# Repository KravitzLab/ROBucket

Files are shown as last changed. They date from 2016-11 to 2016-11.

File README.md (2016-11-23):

# ROBucket
```C
PAGE UNDER CONSTRUCTION
```
## What is it?
[description] a low-cost operant chamber based on the Arduino microcontroller

## What's available?
+ <b> ROBucket-wiki </b>  

Other links above:

+ <b>Build instructions</b>  
-Detailed instructions for assembling your own ROBucket!

+ <b>Design files</b>  
-Side panel templates for drilling mounting holes  
-3D design files for interior operant mount

+ <b>Arduino code</b>  
-Various scripts (Arduino sketches) for different experiment paradigms

ROBucket was designed by a team of researchers at the National Institutes of Health, more info here: http://www.kravitzlab.com/

https://tinkercad.com/things/8v2CjPmA2EL

Check out our site [here](https://www.niddk.nih.gov/research-funding/at-niddk/labs-branches/diabetes-endocrinology-and-obesity-branch/eating-addiction-section/rodent-operant-bucket/Pages/default.aspx)

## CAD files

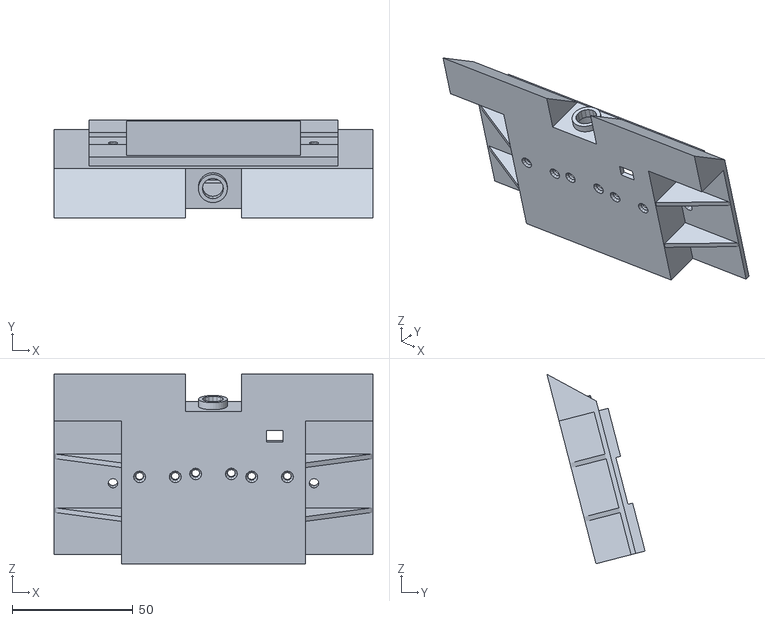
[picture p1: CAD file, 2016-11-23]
Design-files/ROBucket nose poke housing.stl
132.0 x 40.6 x 78.4

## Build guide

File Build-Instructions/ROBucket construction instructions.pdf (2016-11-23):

# Instructions for Constructing a Rodent Operant Bucket (ROBucket)

### Required Parts

Part | Quantity Source | Total Price
4 quart square container (6.5" x 6.5" x 8") | 1 | U.S. Plastic Corp | $5.97
Lid for 2- and 4-quart containers | 1 | U.S. Plastic Corp | $1.42
Arduino UNO - R3 | 1 | SparkFun Electronics | $24.95
LCD keypad shield for Arduino | 1 | DFRobot | $14.55
Adafruit assembled data logging shield for Arduino | 1 | Adafruit Industries | $19.95
Kingston 4GB microSD high capacity (microSDHC) card | 1 | Office Depot | $8.99
Photo interrupter board with GP1A57HRJ00f | 3 | Karlsson Robotics | $14.97
Sainsmart 2-channel 5V relay module | 1 | O'Neill Computer Products | $18.99
12 VDC solenoid valve | 1 | American Science & Surplus | $3.25
Clear acrylic squares 1/2" acrylic square | 1 | U.S. Plastic Corp | $0.24
JST SH jumper 3 wire assembly - 8" | 3 | SparkFun Electronics | $4.05
Faceplate, 3 port | 1 | Zoro Tools | $7.91
Machine screw,flat,4-40x1/2 L, nylon | 8 | Zoro Tools | $0.32
Hex nut, machine screw, 4-40, black, nylon | 12 | Zoro Tools | $0.32
Wall adapter power supply - 9VDC 650mA | 1 | SparkFun Electronics | $5.95
DC barrel jack adapter - female | 1 | SparkFun Electronics | $2.95
1/2" straight cannula blunt end tip (15 gauge) | 1 | Fisnar | $0.24
Male luer with lock ring x 1/8" hose barb, nylon | 1 | Cole-Parmer | $0.34
Male luer with lock ring x female luer coupler, PC | 1 | Cole-Parmer | $0.56
BD 20mL syringe with Luer-Lok tip | 1 | Allegro Medical | $0.51
Masterflex platinum-cured silicone tubing, L/S 16, 25 ft. | 0.5 Ft | Cole-Parmer | $1.18
Stor-All broom clip | 2 | Aubuchon Hardware | $3.38
Jumper wires premium 6" F/F | 9 | SparkFun Electronics | $2.99
Wing nut,6-32 | 2 | Grainger | $1.07
Machine screw, flat, SS, 6-32x1.5 L | 2 | Grainger | $0.29
2-way 2.1mm DC barrel jack splitter squid | 1 | Adafruit Industries | $2.95
0.1" (2.54mm) crimp connector housing: 1x1-pin | 9 | Karlsson Robotics | $0.21
Female crimp pins for 0.1" housings | 9 | Karlsson Robotics | $0.54
3D printed housing | 1 | Makerbot Replicator 2 Desktop 3D Printer | Variable
Total | | | $149.19

Step 1: Drilling holes in the bucket
1. Print out the Adobe Illustrator files for the front and side panel on plain paper or removable labels (8½” x 11”).
2. Place the templates on the bucket, with the side panel to the right of the front panel.
3. Drill seven 1

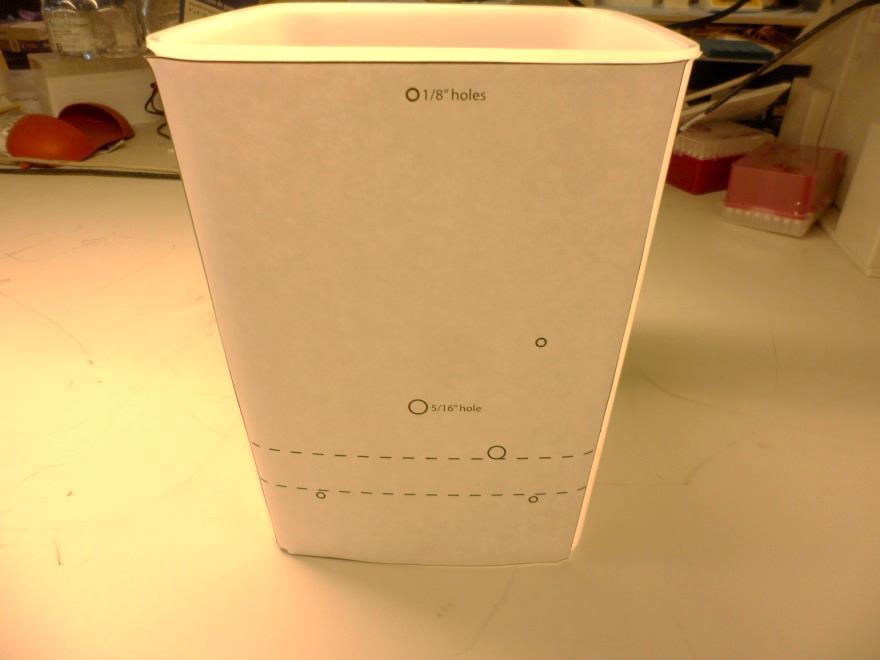
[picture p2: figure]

/8” holes and two 5
/16” holes where shown on the templates.
Step 2: Assembling the nose poke and drinking well enclosure

In this step, we will assemble the nose poke and drinking well enclosure and attach it to the inside of the bucket.

1. Print out the 3D housing. We used Makerbot PLA material and printed at a high resolution.

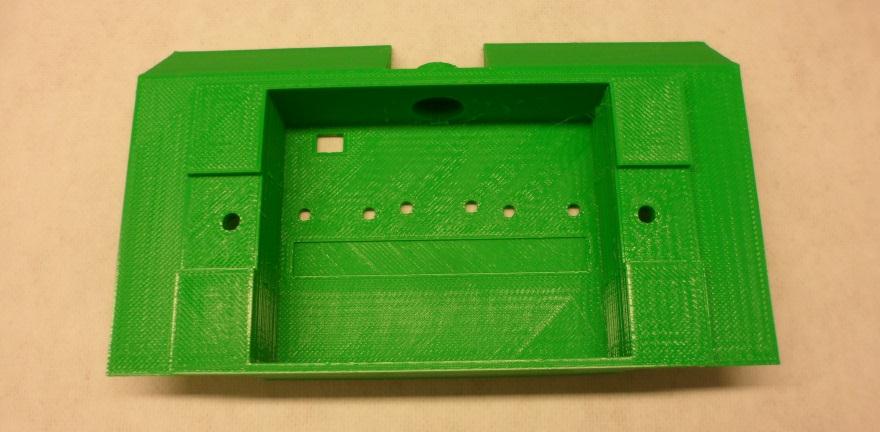
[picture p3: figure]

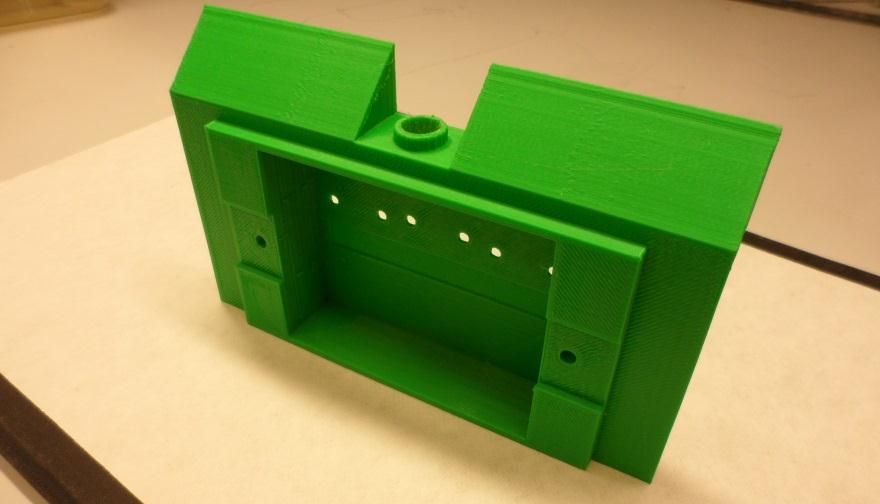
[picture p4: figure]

2. Plug three JST SH jumper 3-wire assemblies into three photo interrupter boards. Label the signal wire for each “L” (for left), “C” (for center), and “R” (for right).

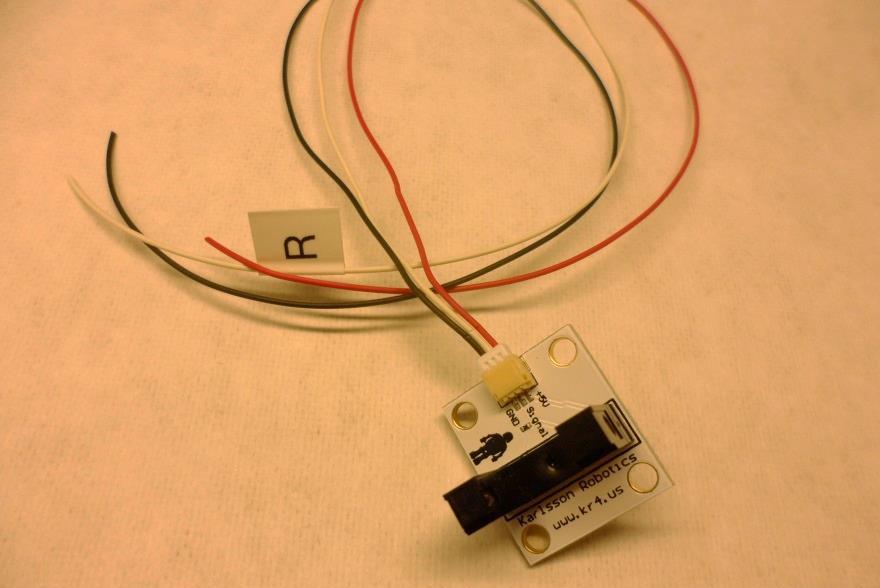
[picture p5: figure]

3. Use the nylon screws and hex nuts to secure the photo interrupter boards to the inside of the 3D printed cover and bring the wires to the outside of the cover using the hole in the top left of the housing.

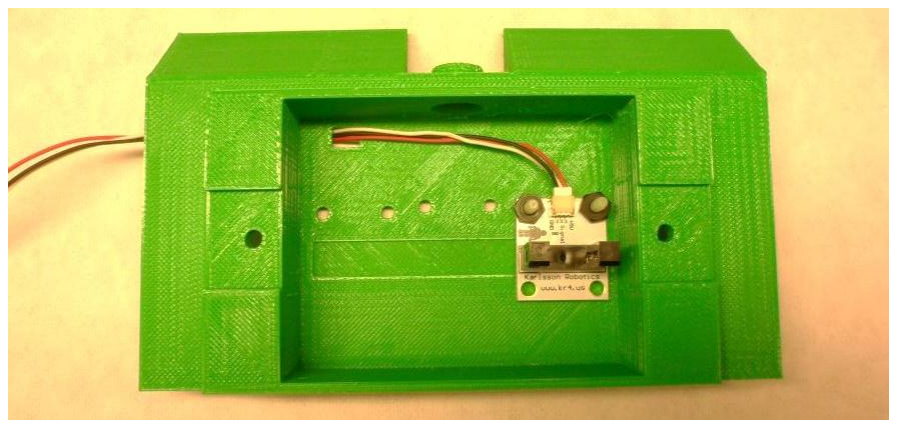
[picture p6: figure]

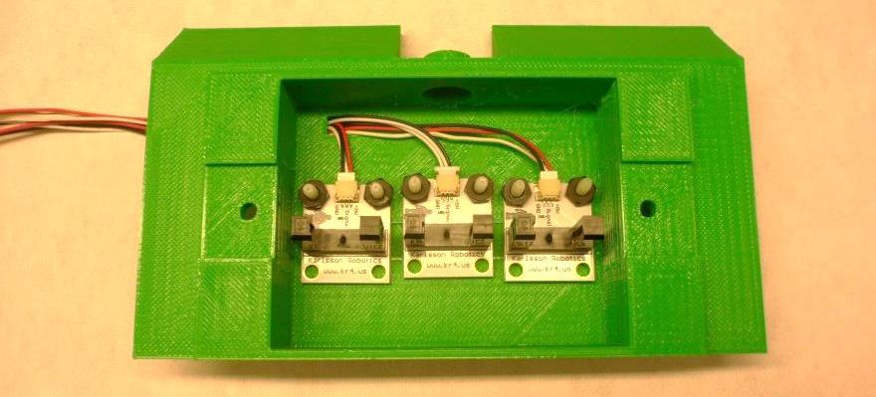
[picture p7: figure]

4. Assemble the blunt needle with the two luer lock pieces, and screw together securely in the top hole in the housing.

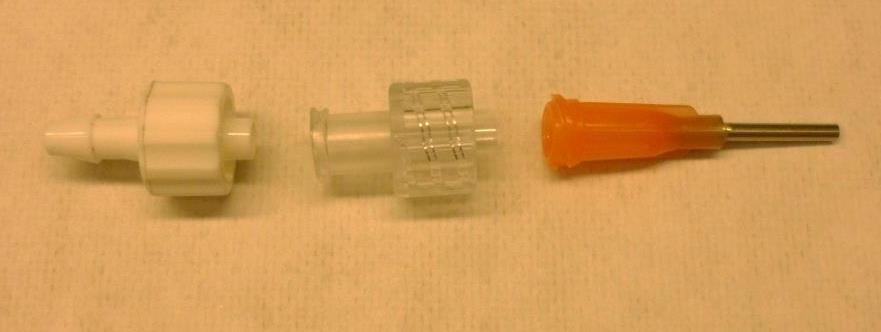
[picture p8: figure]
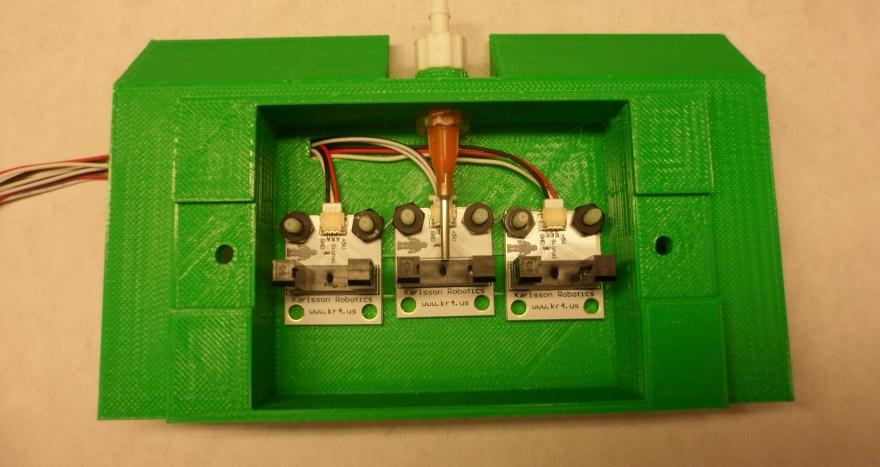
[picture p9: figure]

5. Place the ½” piece of plastic under the center poke.

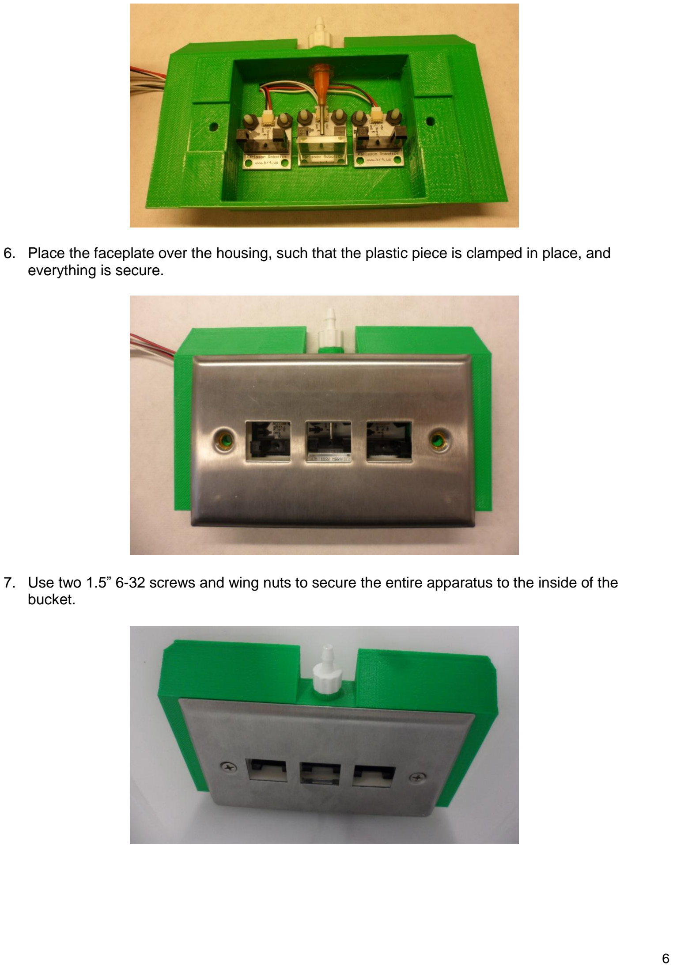
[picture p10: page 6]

6. Place the faceplate over the housing, such that the plastic piece is clamped in place, and everything is secure.
7. Use two 1.5” 6-32 screws and wing nuts to secure the entire apparatus to the inside of the bucket.

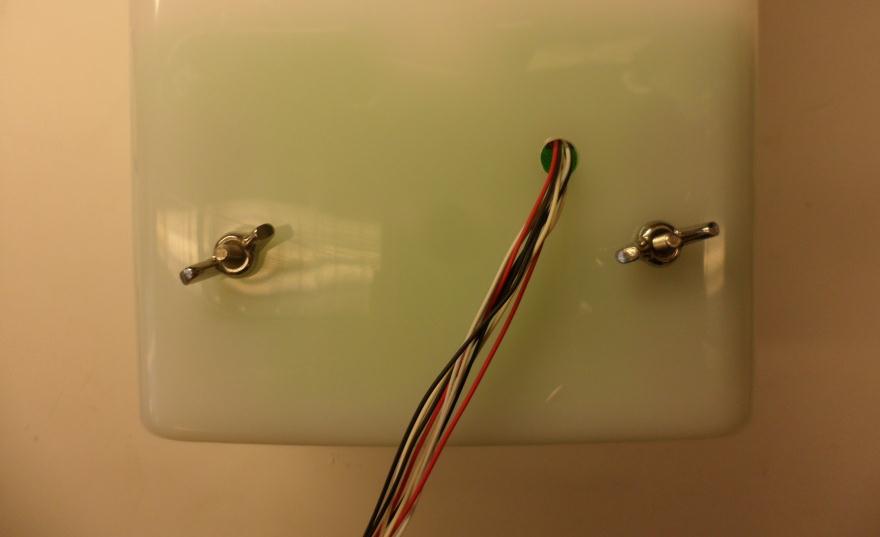
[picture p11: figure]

Step 3. Mounting the solenoid valve

In this step, we will mount the solenoid valve and liquid syringe on the outside side of the bucket.

1. Using nylon screws and hex nuts, attach the two broom clips to the two 5/16” holes on the side of the bucket.

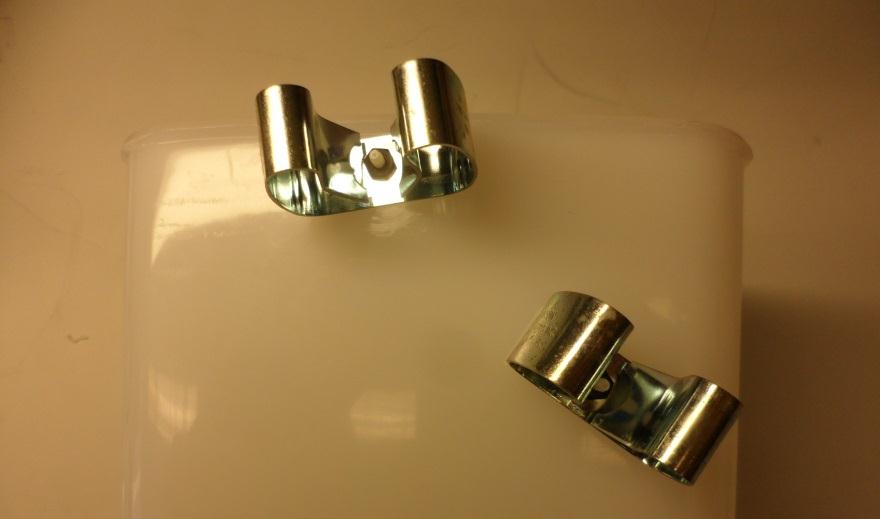
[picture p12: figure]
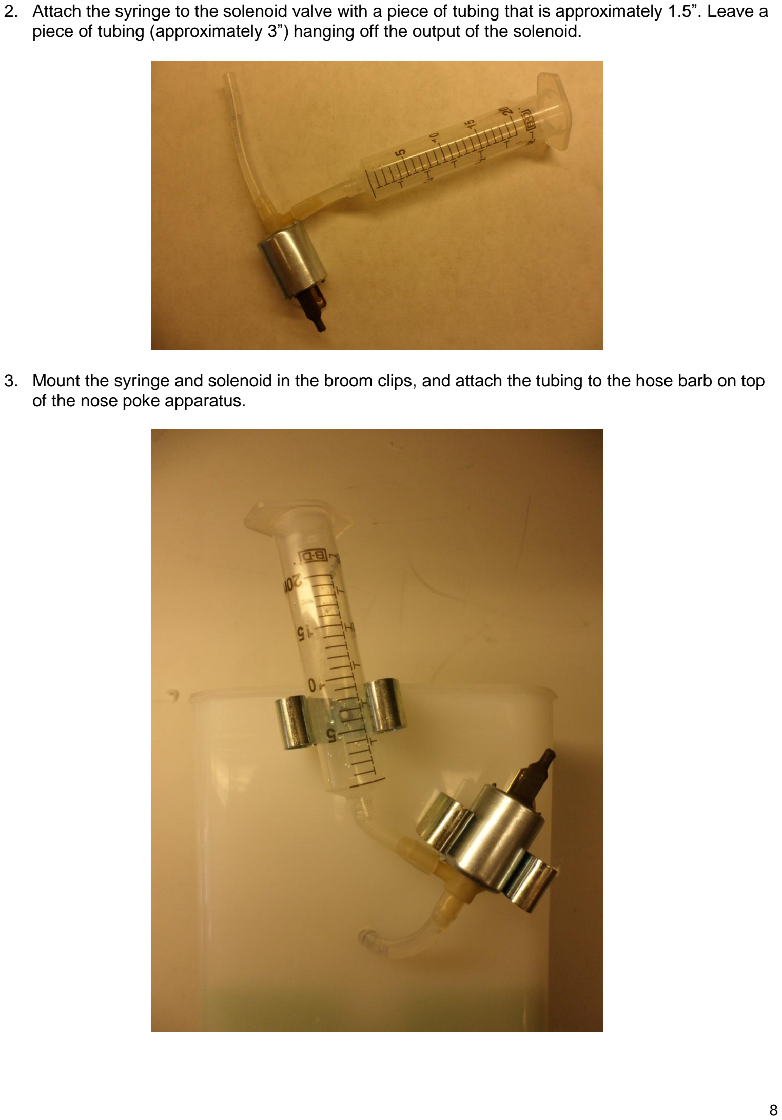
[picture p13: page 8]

2. Attach the syringe to the solenoid valve with a piece of tubing that is approximately 1.5”. Leave a piece of tubing (approximately 3”) hanging off the output of the solenoid.
3. Mount the syringe and solenoid in the broom clips, and attach the tubing to the hose barb on top of the nose poke apparatus.

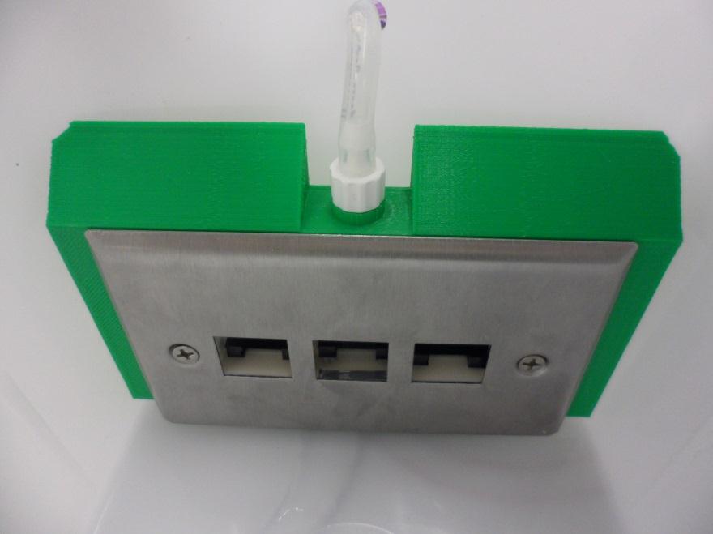
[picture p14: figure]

Step 4. Assembling the side panel electronics

In this step, we will assemble the side panel electronics and attach them to the outside front of the bucket.

1. Place the Arduino Uno so that the top right and bottom left mounting holes align with the top two holes in the side panel. Secure the Arduino board in place using the nylon screws and hex nuts. Place an additional hex nut between the bucket and the board at each mounting point, to allow for a small space between the Arduino and the bucket.

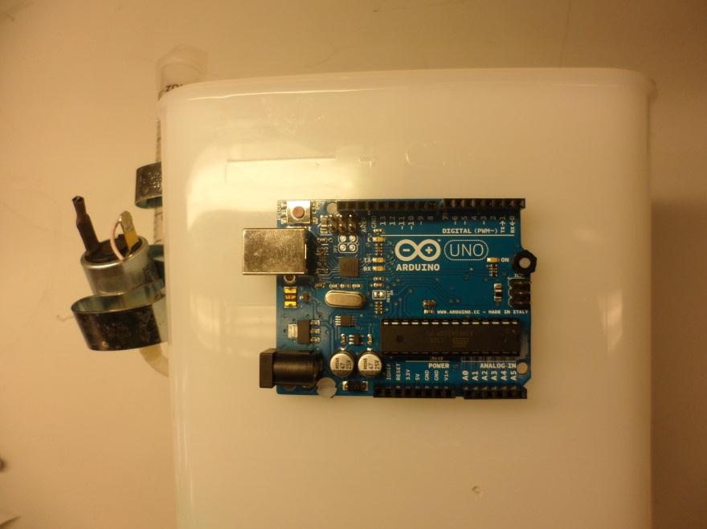
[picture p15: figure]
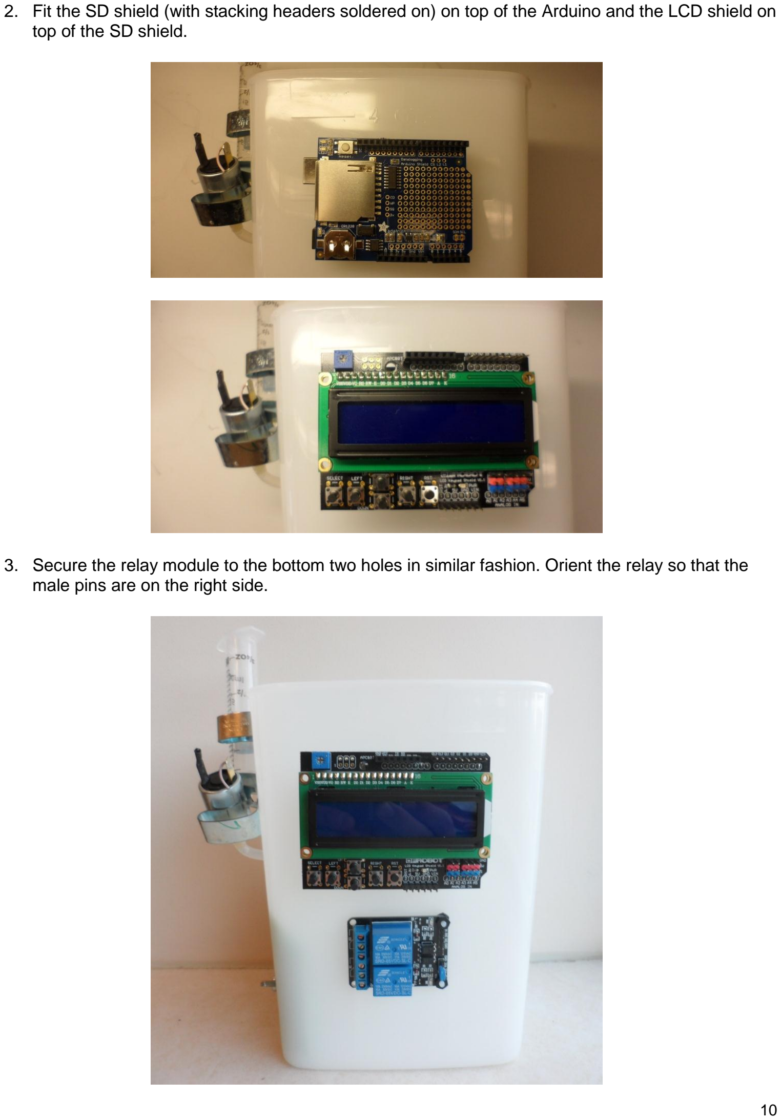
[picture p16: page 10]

2. Fit the SD shield (with stacking headers soldered on) on top of the Arduino and the LCD shield on top of the SD shield.
3. Secure the relay module to the bottom two holes in similar fashion. Orient the relay so that the male pins are on the right side.

Step 5. Wiring up the front electronics
In this step, we will wire up the front electronics.
1. Place three short pieces of heat shrink tubing around the bundle of 9 wires coming from the nose poke apparatus. Do not heat shrink these yet.

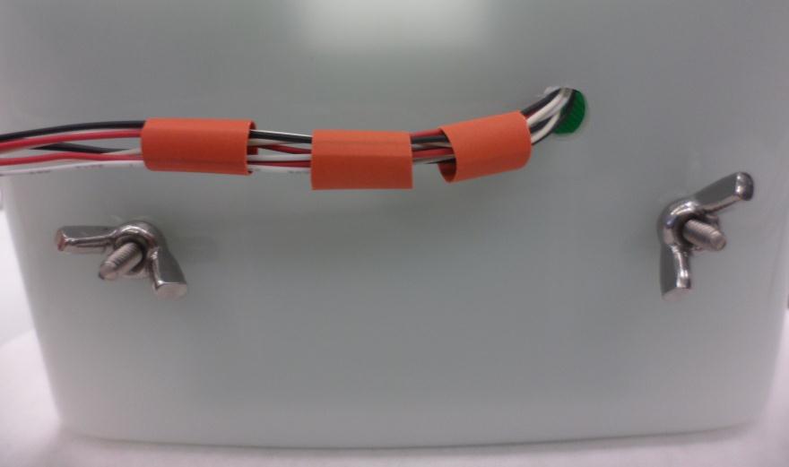
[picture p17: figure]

2. Route this bundle of wires underneath the relay module (you may want to unscrew it to do this).

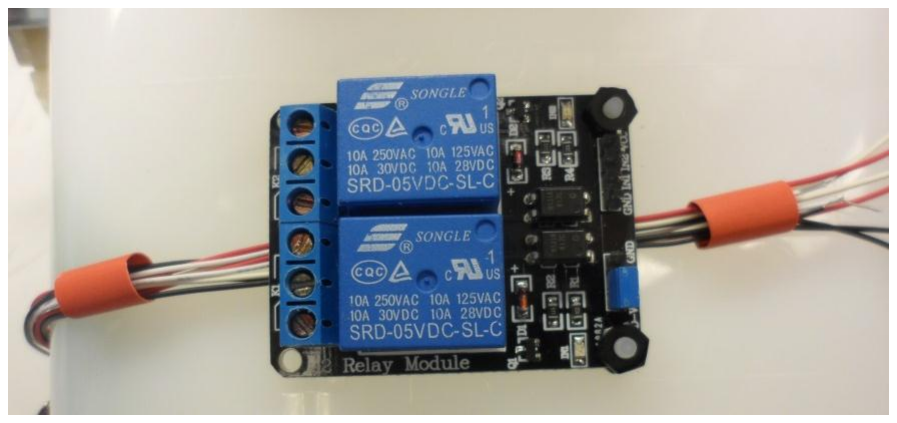
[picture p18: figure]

3. If these wires are long enough to reach the LCD keypad shield, place a crimp connector on the end of each.

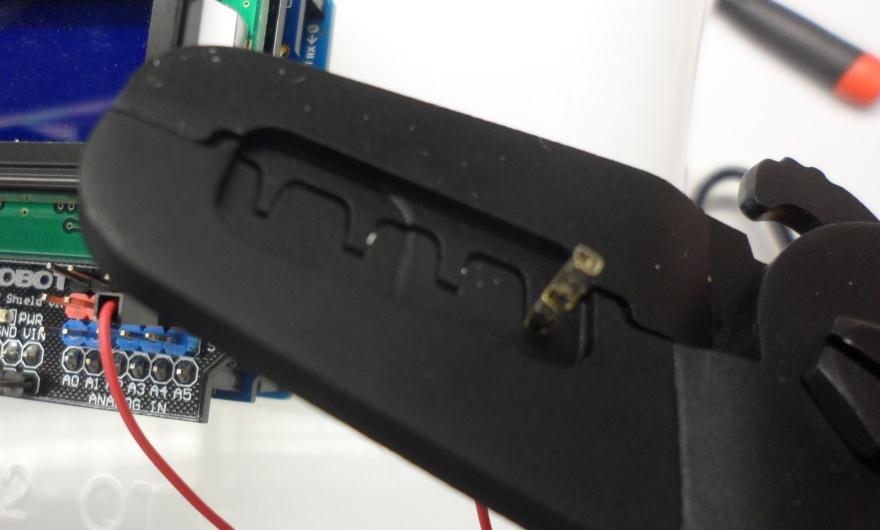
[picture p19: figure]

4. If any wires are not long enough, solder a header wire with a crimp connector on it to increase the length so it can reach.

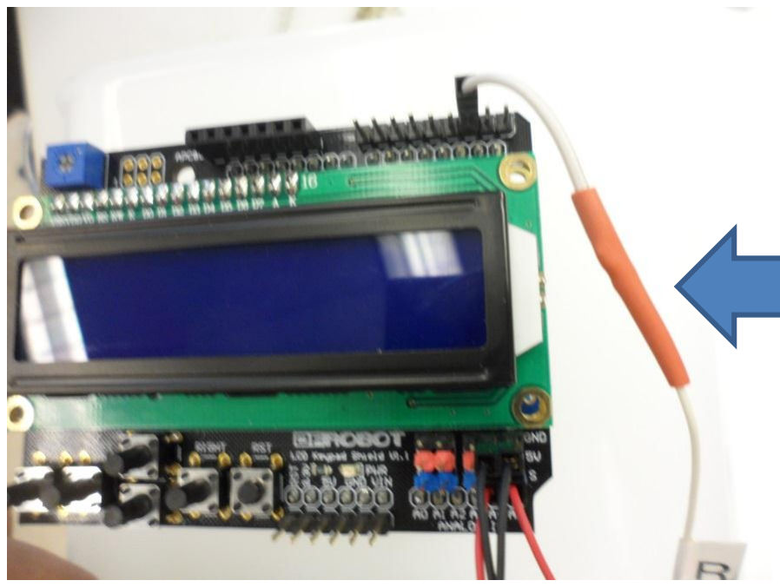
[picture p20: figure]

5. Plug the power and ground wires from the three nose pokes (6 wires total) into the power distributor on the LCD shield, such that each one has its own power and ground.

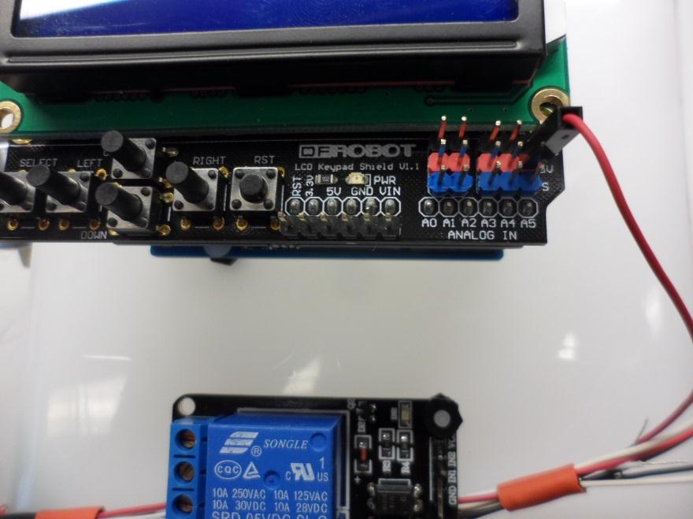
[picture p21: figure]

6. Plug the remaining 3 wires from the nose poke enclosure into the input/output pins at the top of the LCD shield, in the following order:
Pin 0: Active poke (left)
Pin 1: Drinking well (center)
Pin 2: Inactive poke (right)
7. Use three F/F jumper wires to connect the relay module to the GND and 5V pins on the LCD shield, and attach IN1 on the relay module to Pin 3 on the LCD shield.

Step 6. Wiring up the solenoid (almost done!)
1. Cut and strip one red wire approximately 7” long, and one red and one black wire, each approximately 4.5” long.
2. Solder the long red wire, and one of the black wires onto the solenoid, and heat shrink terminals.

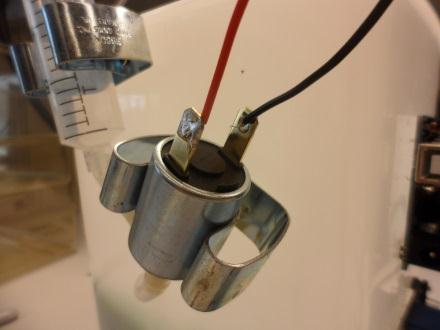
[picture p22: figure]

3. Screw the long red wire into the bottom port of the relay module, and the short red wire into the port that’s 2nd from the bottom.

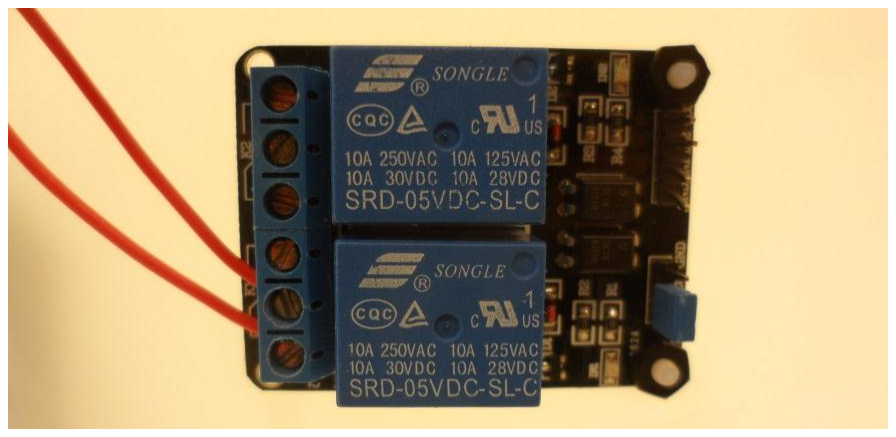
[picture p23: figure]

4. Screw the black wire from the solenoid, and the short red wire into the DC barrel jack.

5. Plug the barrel jack Y adapter into the DC barrel jack and the Arduino power input, and attach to a 9V DC, 650 mA power supply.

### 6. You’re done!

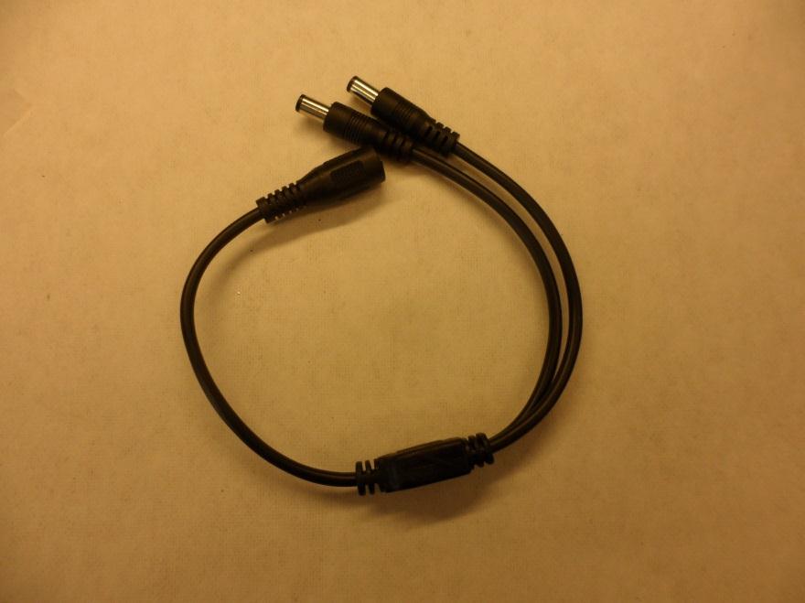
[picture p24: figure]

Step 7: Uploading the ROBucket program and testing the hardware
1. Download the ROBucket sketch from the website. Robucket_1poke.ino is for ROBuckets that only have an active poke and a drinking well, whereas Robucket_2pokes.ino is for ROBuckets that have both an active and inactive poke.
2. Upload the sketch to the Arduino Uno with a USB (Type B) cable.
3. Insert an SD or microSD card into the data logging shield before turning the ROBucket on. ROBucket will display an error message (“Card Failed”) unless there is a functional SD card in the data logging shield.
4. Fill the syringe with water.
5. Power up the ROBucket. The first time you fill the syringe with water, you might need to hit the Reset button on the LCD shield a few times to run the water through the tubing.
6. Push the Up button to start the FR1 program.
7. Check that all three pokes register on the LCD screen, that the active poke dispenses water into the drinking well, and that the data is being properly logged onto the SD card.

# ROBucket Wiring Diagram

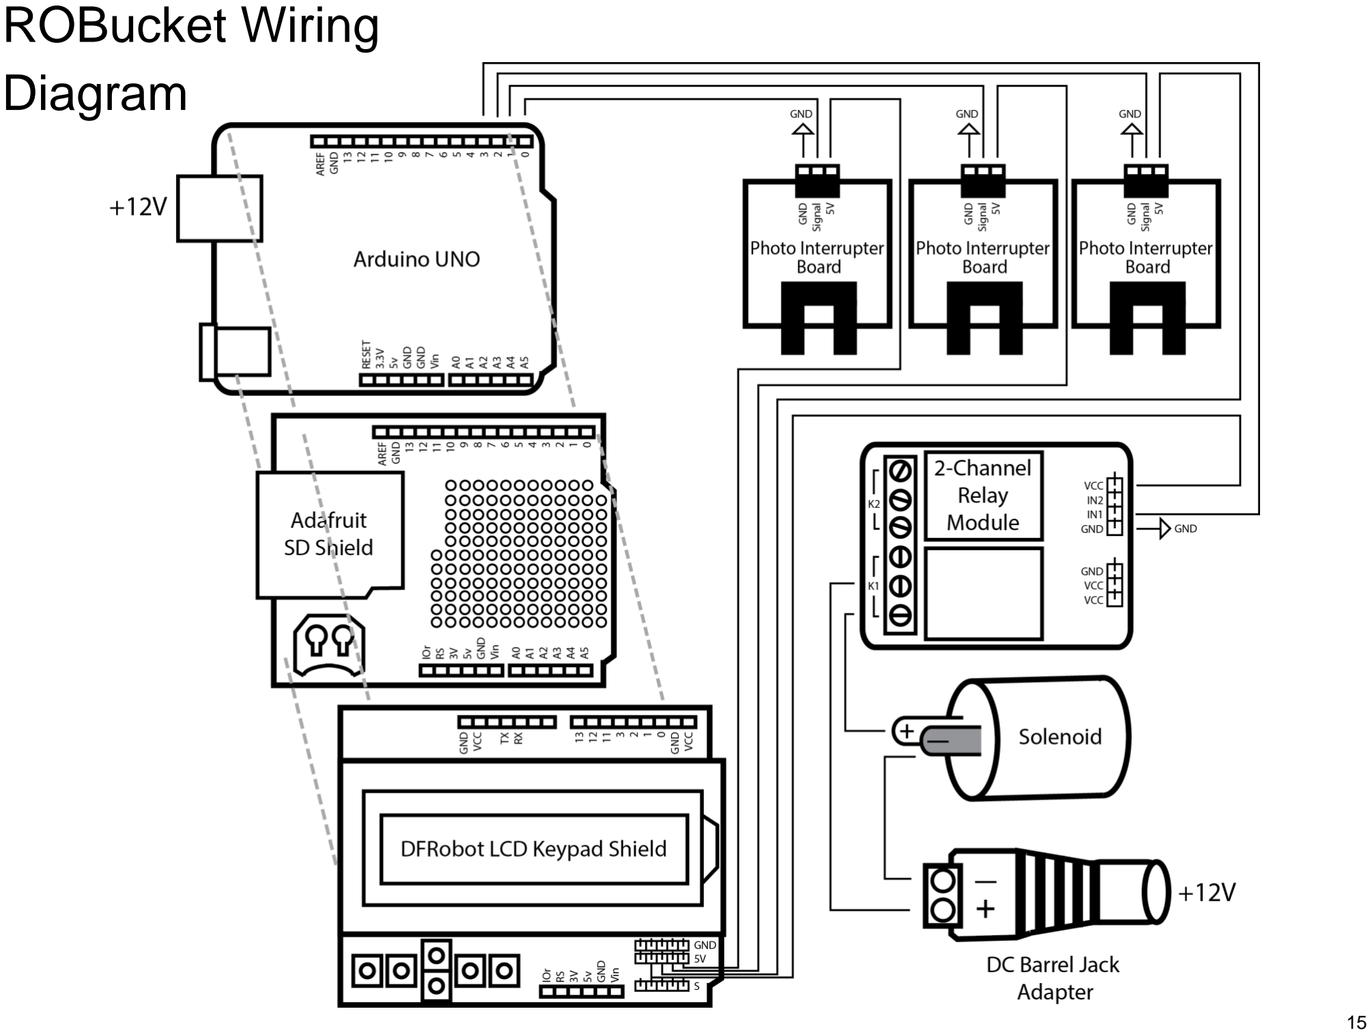
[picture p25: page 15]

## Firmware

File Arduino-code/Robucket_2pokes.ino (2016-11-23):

 #include <Wire.h>                                         // reference the Wire and LiquidCrystal libraries
 #include <LiquidCrystal.h>
 #include <SD.h>
 #include "RTClib.h"

const int activePin = 0;
const int drinkPin = 1; 
const int inactivePin = 2;
const int sugarPin = 3;
const int CS_pin = 10;

RTC_DS1307 RTC;

String year, month, day, hour, minute, second, date, time;

const int sugarAmt = 100;                                  // open the solenoid for 50 ms (controls amount of sucrose solution)
int timeOut = 1;                                    // set the timeout period between pokes to 1s

int activeState = 0;                                         // initialize counter variables to 0
int lastActiveState = 0;
int activeCount = 0;
int lastActiveCount = 0;
int inactiveState = 0;
int lastInactiveState = 0;
int inactiveCount = 0;
int drinkState = 0;
int lastDrinkstate = 0;
int drinkCount = 0;
int pelletNumber = 1;
              
int pokeTime = 0;                            
int ipokeTime = 0;
int startTime = 0;
long previousMillis = 0; 
int x = 0;

LiquidCrystal lcd( 8, 9, 4, 5, 6, 7 );
int ratio = 0;
int program = 0;

int logData() {
  DateTime datetime = RTC.now();
  year = String(datetime.year(), DEC);
  month = String(datetime.month(), DEC);
  day  = String(datetime.day(),  DEC);
  hour  = String(datetime.hour(),  DEC);
  minute = String(datetime.minute(), DEC);
  second = String(datetime.second(), DEC);
 
  //Concatenate the strings into date and time
  time = month + "/" + day + " " + hour + ":" + minute + ":" + second;
  
  File dataFile = SD.open("RoBucket.csv", FILE_WRITE);
  if (dataFile) {   
    dataFile.print(ratio);
    dataFile.print(",");
    dataFile.print(time);
    dataFile.print(",");
    dataFile.print(pelletNumber-1);
    dataFile.print(",");
    dataFile.print(activeCount);
    dataFile.print(",");
    dataFile.print(inactiveCount);
    dataFile.print(",");
    dataFile.println(drinkCount);
    dataFile.close();
  }
}

int deliverSugar() {
  lcd.setCursor(14, 0);            // move the LCD cursor to row 2, column 5
  lcd.print(pelletNumber);           // update the nosepoke count on the LCD
  digitalWrite(sugarPin, HIGH);   // send 5 volts through the sugar delivery pin
    lastActiveCount = activeCount;
  pelletNumber = pelletNumber + 1;
  delay(sugarAmt);
  if (program == 4) {
     ratio = round ((5 * exp (0.2 * pelletNumber)) - 5);
  }
  digitalWrite(sugarPin, LOW);
  delay(200);
}

void setup() {                
  // initialize the digital pins as output and input
  pinMode(activePin, INPUT_PULLUP);
  pinMode(drinkPin, INPUT);
  pinMode (inactivePin, INPUT);
  pinMode (sugarPin, OUTPUT);
  pinMode (CS_pin, OUTPUT);
  
  Wire.begin();
  RTC.begin();
  
  // set up the LCD
  lcd.begin(16, 2);
  lcd.clear();
  
  if (!SD.begin(CS_pin)) {
    lcd.print("Card Failed");
    while(1) {}
    }
  
  else {
  lcd.print("Up=FR1 Rght=Mag");
  lcd.setCursor(0,1);
  lcd.print("Down=FR5 Left=PR");
  
  File dataFile = SD.open("RoBucket.csv", FILE_WRITE);
  if (dataFile) {
    dataFile.println("Program,Time,Sugar Deliveries,Active Pokes,Inactive Pokes,Well Entries");
    dataFile.close();
    }
  }
}

void loop() { 
  if (analogRead(0) < 50) {
    lcd.clear();
    lcd.print("Mag");
    lcd.setCursor(12,0);
    lcd.print("S:0");
    lcd.setCursor(0,1);
    lcd.print("A:0  I:0  W:0");
    startTime = millis()/1000;
    program = 2;
    ratio = random(45,75);
   }
  else if (analogRead(0) < 400) {
    lcd.clear();
    lcd.print("FR1");
    lcd.setCursor(12,0);
    lcd.print("S:0");
    lcd.setCursor(0,1);
    lcd.print("A:0  I:0  W:0");
    startTime = millis()/1000;
    program = 1;
    ratio = 1;
  }
  else if (analogRead(0) < 600) {
    lcd.clear();
    lcd.print("FR5");
    lcd.setCursor(12,0);
    lcd.print("S:0");
    lcd.setCursor(0,1);
    lcd.print("A:0  I:0  W:0");
    startTime = millis()/1000;
    program = 3;
    ratio = 5;
  }
  else if (analogRead(0) < 650) {
    lcd.clear();
    lcd.print("PR");
    lcd.setCursor(12,0);
    lcd.print("S:0");
    lcd.setCursor(0,1);
    lcd.print("A:0  I:0  W:0");
    startTime = millis()/1000;
    program = 4;
    ratio = round ((5 * exp (0.2 * pelletNumber)) - 5);
   }
  
  long t = millis()/1000 - startTime;
  
  String timeStamp;
      int h = t / 3600;
      timeStamp += h;
      timeStamp += ":";
      t = t % 3600;
      int m = t / 60;
      timeStamp += m;
      timeStamp += ":";
      int s = t % 60;
      timeStamp += s;
   
  activeState = digitalRead(activePin);  // define activeState as the readout of the nosepoke pin
  inactiveState = digitalRead(inactivePin);
  drinkState = digitalRead(drinkPin);
   
    // this portion will act as a seconds clock
    unsigned long currentMillis = millis();                   // define currentMillis
    if(currentMillis - previousMillis > 1000)             // if the specified time interval has passed...
    {
      previousMillis = currentMillis;                         // save the last time you showed time
      lcd.setCursor(4,0);                                    // bring the cursor to the first row, column 11
    
      if (program > 0) {
      lcd.print(timeStamp);                                        // display time
      if (x < 1) {
        logData();
        x=x+1;
      }
      }
    }
    
    if (program == 1) {
      if (activeState != lastActiveState) {
        if (activeState == LOW) {
          activeCount = activeCount + 1;
          lcd.setCursor(2,1);
          lcd.print(activeCount);
          if (activeCount - lastActiveCount >= ratio && t - pokeTime >= timeOut) {
            pokeTime = t;
            deliverSugar();
          }
          logData();
        }
        lastActiveState = activeState;
      }

    }
    
    if (program == 3 || program == 4) {
      if (activeState != lastActiveState) {
        if (activeState == LOW && t - pokeTime >= timeOut) {
          activeCount = activeCount + 1;
          lcd.setCursor(2,1);
          lcd.print(activeCount);
          pokeTime = t;
          if (activeCount - lastActiveCount >= ratio) {
            deliverSugar();
          }
          logData();
        }
        lastActiveState = activeState;
    }
    }
    if (program == 4 && t > 3600 || program == 4 && t - pokeTime > 300) {
      File dataFile = SD.open("RoBucket.csv", FILE_WRITE);
        if (dataFile) {   
          dataFile.print("FINAL");
          dataFile.print(",");
          dataFile.print(timeStamp);
          dataFile.print(",");
          dataFile.print(pelletNumber-1);
          dataFile.print(",");
          dataFile.print(activeCount);
          dataFile.print(",");
          dataFile.println(drinkCount);
          dataFile.close();  
      while(1) { }
      }
  }  
  if (program == 2) {
    if (t - pokeTime >= ratio) {
      deliverSugar();
      logData();
      pokeTime = t;
      ratio = random(45,75);
    }  
    
    if (activeState != lastActiveState) {
        if (activeState == LOW) {
          activeCount = activeCount + 1;
          lcd.setCursor(2,1);
          lcd.print(activeCount);
          logData();
        }
        lastActiveState = activeState;
    }
    }
   
    if (drinkState != lastDrinkstate) {
     if (drinkState == LOW) {
       drinkCount = drinkCount + 1;
       lcd.setCursor (12, 1);
       lcd.print(drinkCount);
       logData();
     }
     lastDrinkstate = drinkState;
   }
   
   if (inactiveState != lastInactiveState) {
     if (inactiveState == LOW) {
       inactiveCount = inactiveCount + 1;
       lcd.setCursor (7, 1);
       lcd.print(inactiveCount);
       logData();
     }
     lastInactiveState = inactiveState;
   }
    
   if (analogRead(0) < 900 && analogRead(0) > 750) {
      File dataFile = SD.open("RoBucket.csv", FILE_WRITE);
      if (dataFile) {   
        dataFile.print("FINAL");
        dataFile.print(",");
        dataFile.print(timeStamp);
        dataFile.print(",");
        dataFile.print(pelletNumber-1);
        dataFile.print(",");
        dataFile.print(activeCount);
        dataFile.print(",");
        dataFile.print(inactiveCount);
        dataFile.print(",");
        dataFile.println(drinkCount);
        dataFile.close();
      }
   while(1) {};
   }
}
